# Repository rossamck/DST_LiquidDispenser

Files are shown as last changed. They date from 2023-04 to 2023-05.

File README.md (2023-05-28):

# GUSTAVO - Liquid Dispensing Client

This repo hosts the software and schematics for the GUSTAVO project.

## Installation
### Building from Source

1. Clone this repository:

```bash
git clone https://github.com/rossamck/DST_LiquidDispenser.git
```

2. Navigate to the project directory:
```bash
cd DST_LiquidDispenser
```

3. Install dependencies: 
```bash
npm install
```

4. Run the application:
```bash
npm start
```

### Running release application
1. Download the appropriate installation file for your operating system from the [Releases](https://github.com/rossamck/DST_LiquidDispenser/releases) page.

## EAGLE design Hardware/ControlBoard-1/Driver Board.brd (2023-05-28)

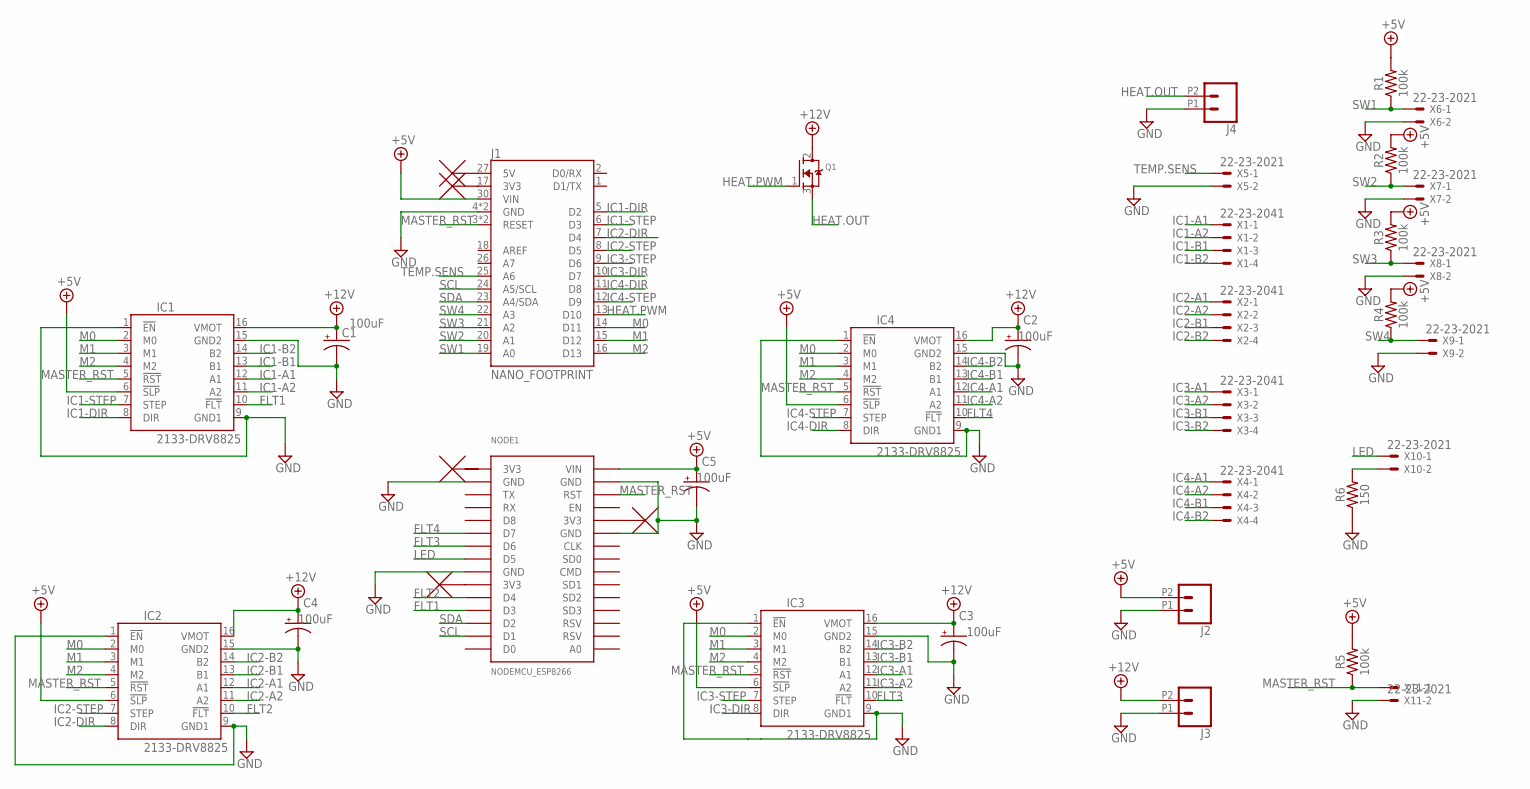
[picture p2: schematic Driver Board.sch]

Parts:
C1, C2, C3, C4, C5: CPOL-USD; PANASONIC_D
IC1, IC2, IC3, IC4: 2133-DRV8825; DRV8825
J1: NANO_FOOTPRINT; NANO
J2, J3, J4: CONN_02SCREWTERMINAL-6.35MM-2; 1X02_6.35_SCREWTERM
NODE1: NODEMCU_ESP8266
Q1: MOSFET-NGDS_TO220V; TO220V
R1, R2, R3, R4, R5: 100k; 0805
R6: 150; 0805
X1, X2, X3, X4: 22-23-2041
X5, X6, X7, X8, X9, X10, X11: 22-23-2021

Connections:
3V3: NODE1.3V3@1 (3V3)
+5V: C5.+, IC1.6 (!SLP), IC2.6 (!SLP), IC3.6 (!SLP), IC4.6 (!SLP), J1.30 (VIN), J2.P2 (1), NODE1.VIN, R1.2, R2.2, R3.2, R4.2, R5.2
+12V: C1.+, C2.+, C3.+, C4.+, IC1.16 (VMOT), IC2.16 (VMOT), IC3.16 (VMOT), IC4.16 (VMOT), J3.P2 (1), Q1.2 (D)
FLT1: IC1.10 (!FLT), NODE1.D3
FLT2: IC2.10 (!FLT), NODE1.D4
FLT3: IC3.10 (!FLT), NODE1.D6
FLT4: IC4.10 (!FLT), NODE1.D7
GND: C1.-, C2.-, C3.-, C4.-, C5.-, IC1.1 (!EN), IC1.9 (GND1), IC1.15 (GND2), IC2.1 (!EN), IC2.9 (GND1), IC2.15 (GND2), IC3.1 (!EN), IC3.9 (GND1), IC3.15 (GND2), IC4.1 (!EN), IC4.9 (GND1), IC4.15 (GND2), J1.4 (GND), J1.29 (GND), J2.P1 (2), J3.P1 (2), J4.P1 (2), NODE1.GND@1 (GND), NODE1.GND@2 (GND), NODE1.GND@3 (GND), NODE1.GND@4 (GND), R6.1, X5.2, X6.2, X7.2, X8.2, X9.2, X11.2
HEAT.OUT: J4.P2 (1), Q1.3 (S)
HEAT.PWM: J1.13 (D10), Q1.1 (G)
IC1-A1: IC1.12 (A1), X1.1
IC1-A2: IC1.11 (A2), X1.2
IC1-B1: IC1.13 (B1), X1.3
IC1-B2: IC1.14 (B2), X1.4
IC1-DIR: IC1.8 (DIR), J1.5 (D2)
IC1-STEP: IC1.7 (STEP), J1.6 (D3)
IC2-A1: IC2.12 (A1), X2.1
IC2-A2: IC2.11 (A2), X2.2
IC2-B1: IC2.13 (B1), X2.3
IC2-B2: IC2.14 (B2), X2.4
IC2-DIR: IC2.8 (DIR), J1.7 (D4)
IC2-STEP: IC2.7 (STEP), J1.8 (D5)
IC3-A1: IC3.12 (A1), X3.1
IC3-A2: IC3.11 (A2), X3.2
IC3-B1: IC3.13 (B1), X3.3
IC3-B2: IC3.14 (B2), X3.4
IC3-DIR: IC3.8 (DIR), J1.10 (D7)
IC3-STEP: IC3.7 (STEP), J1.9 (D6)
IC4-A1: IC4.12 (A1), X4.1
IC4-A2: IC4.11 (A2), X4.2
IC4-B1: IC4.13 (B1), X4.3
IC4-B2: IC4.14 (B2), X4.4
IC4-DIR: IC4.8 (DIR), J1.11 (D8)
IC4-STEP: IC4.7 (STEP), J1.12 (D9)
LED: NODE1.D5, X10.1
M0: IC1.2 (M0), IC2.2 (M0), IC3.2 (M0), IC4.2 (M0), J1.14 (D11)
M1: IC1.3 (M1), IC2.3 (M1), IC3.3 (M1), IC4.3 (M1), J1.15 (D12)
M2: IC1.4 (M2), IC2.4 (M2), IC3.4 (M2), IC4.4 (M2), J1.16 (D13)
MASTER_RST: IC1.5 (!RST), IC2.5 (!RST), IC3.5 (!RST), IC4.5 (!RST), J1.3 (RESET), J1.28 (RESET), NODE1.RST, R5.1, X11.1
unnamed: R6.2, X10.2
SCL: J1.24 (A5/SCL), NODE1.D1
SDA: J1.23 (A4/SDA), NODE1.D2
SW1: J1.19 (A0), R1.1, X6.1
SW2: J1.20 (A1), R2.1, X7.1
SW3: J1.21 (A2), R3.1, X8.1
SW4: J1.22 (A3), R4.1, X9.1
TEMP.SENS: J1.25 (A6), X5.1

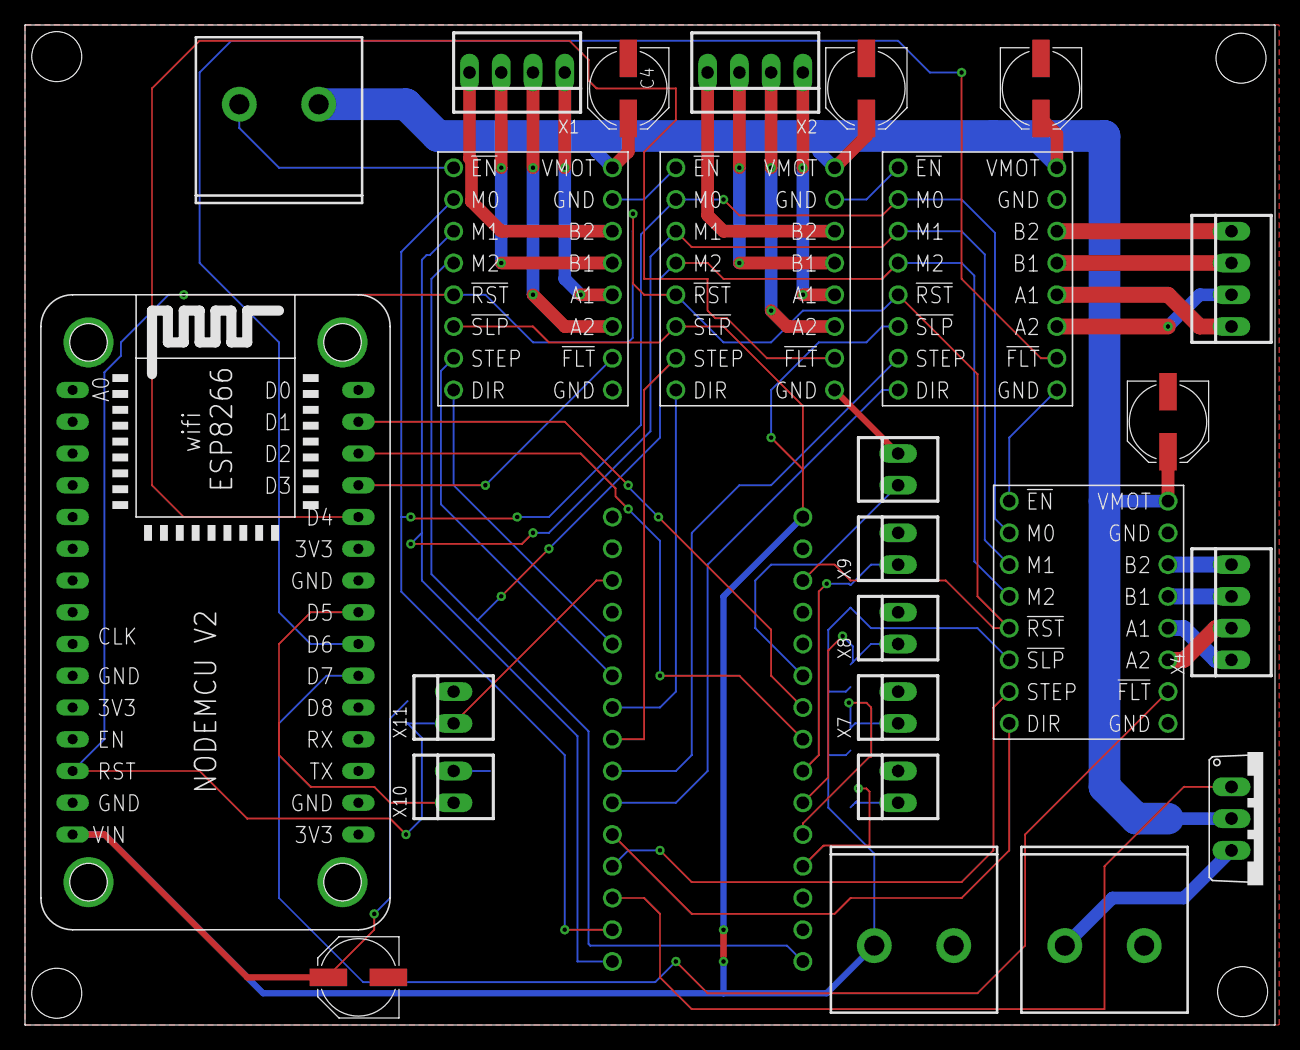
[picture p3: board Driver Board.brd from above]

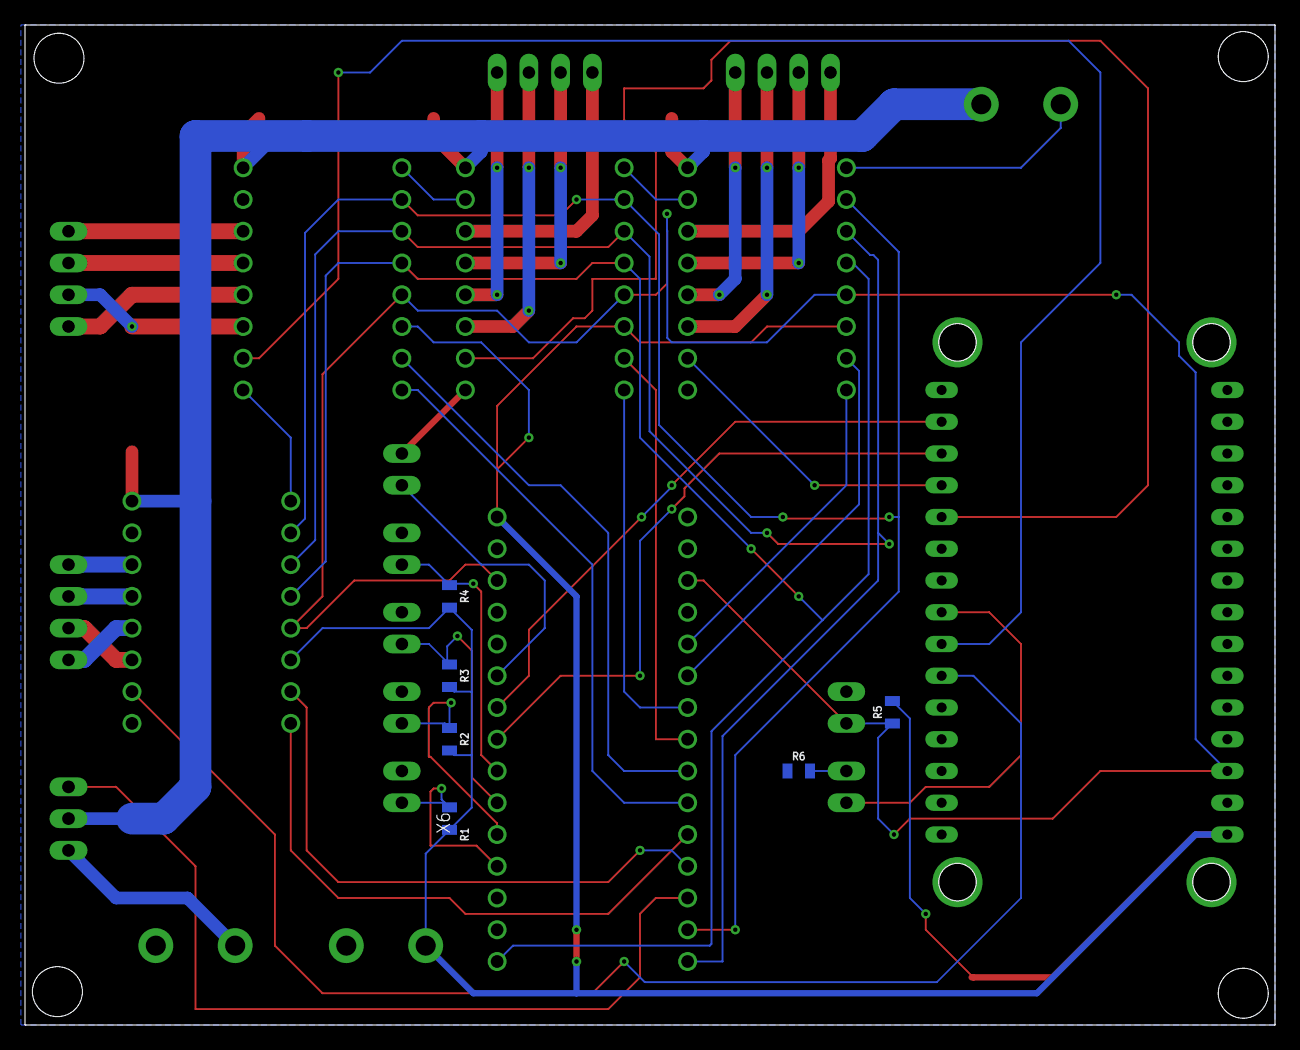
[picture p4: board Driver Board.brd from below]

Board: 2 copper layers, 100.0 x 80.0 mm, 32 parts (6 on the bottom side), 46 nets.

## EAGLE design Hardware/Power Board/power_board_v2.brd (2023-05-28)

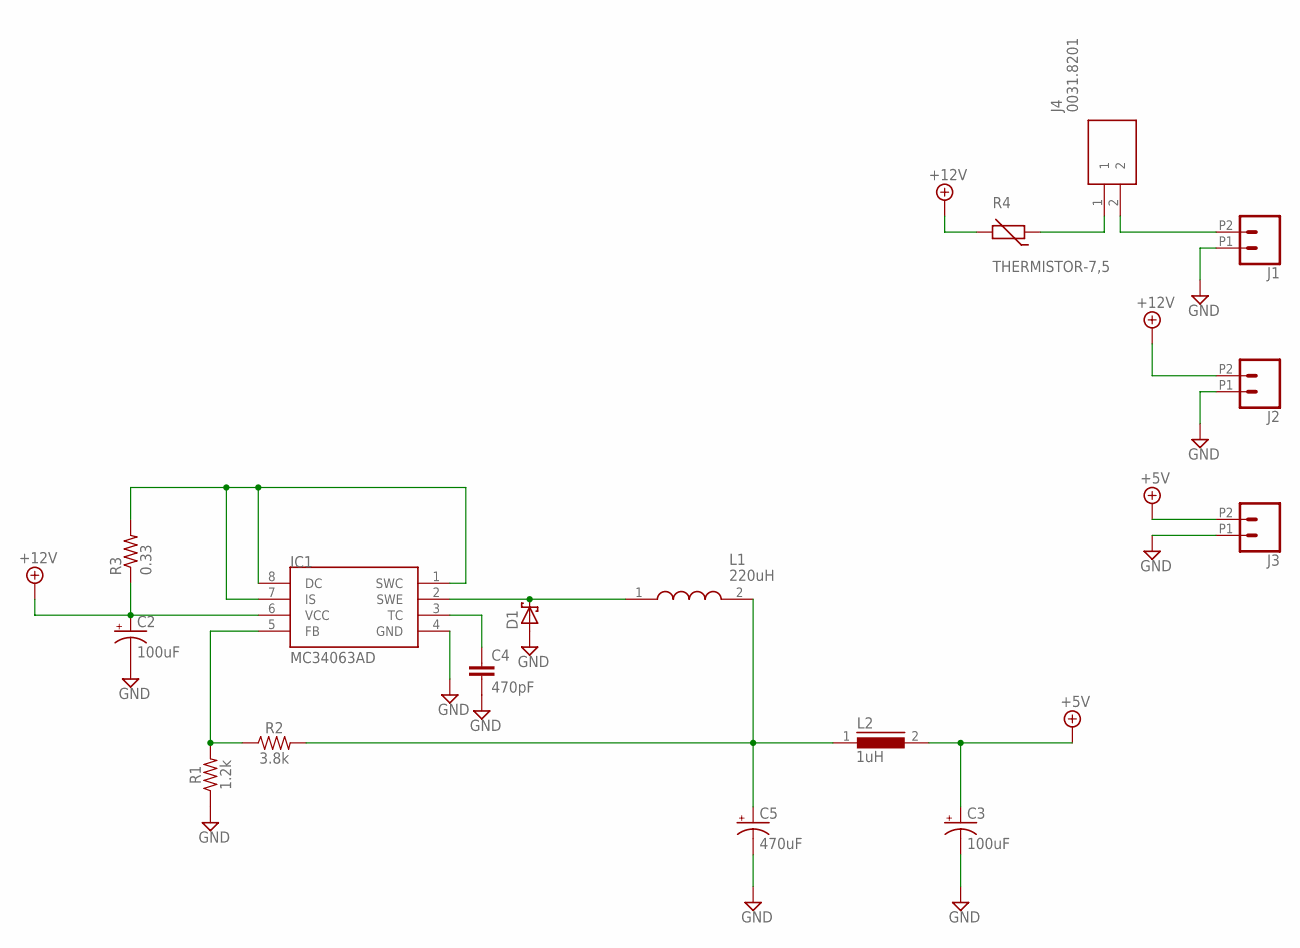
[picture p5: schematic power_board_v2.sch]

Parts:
C2, C3: 100uF; PANASONIC_D
C4: 470pF; C0805
C5: 470uF; PANASONIC_F
D1: SCHOTTKY-DIODEDO41; DO41-10
IC1: MC34063AD; SOIC8
J1, J2, J3: CONN_02SCREWTERMINAL-6.35MM-2; 1X02_6.35_SCREWTERM
J4: 0031.8201
L1: 220uH; WE-TI_809589
L2: 1uH; MICC12
R1: 1.2k; 0805
R2: 3.8k; 0805
R3: 0.33; R2512
R4: THERMISTOR-7,5; R-7,5

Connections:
+5V: C3.+, J3.P2 (1), L2.2
+12V: C2.+, IC1.6 (VCC), J2.P2 (1), R3.1, R4.2
GND: C2.-, C3.-, C4.2, C5.-, D1.A, IC1.4 (GND), J1.P1 (2), J2.P1 (2), J3.P1 (2), R1.1
unnamed: D1.C, IC1.2 (SWE), L1.1
unnamed: C5.+, L1.2, L2.1, R2.2
unnamed: IC1.1 (SWC), IC1.7 (IS), IC1.8 (DC), R3.2
unnamed: C4.1, IC1.3 (TC)
unnamed: IC1.5 (FB), R1.2, R2.1
unnamed: J1.P2 (1), J4.2
unnamed: J4.1, R4.1

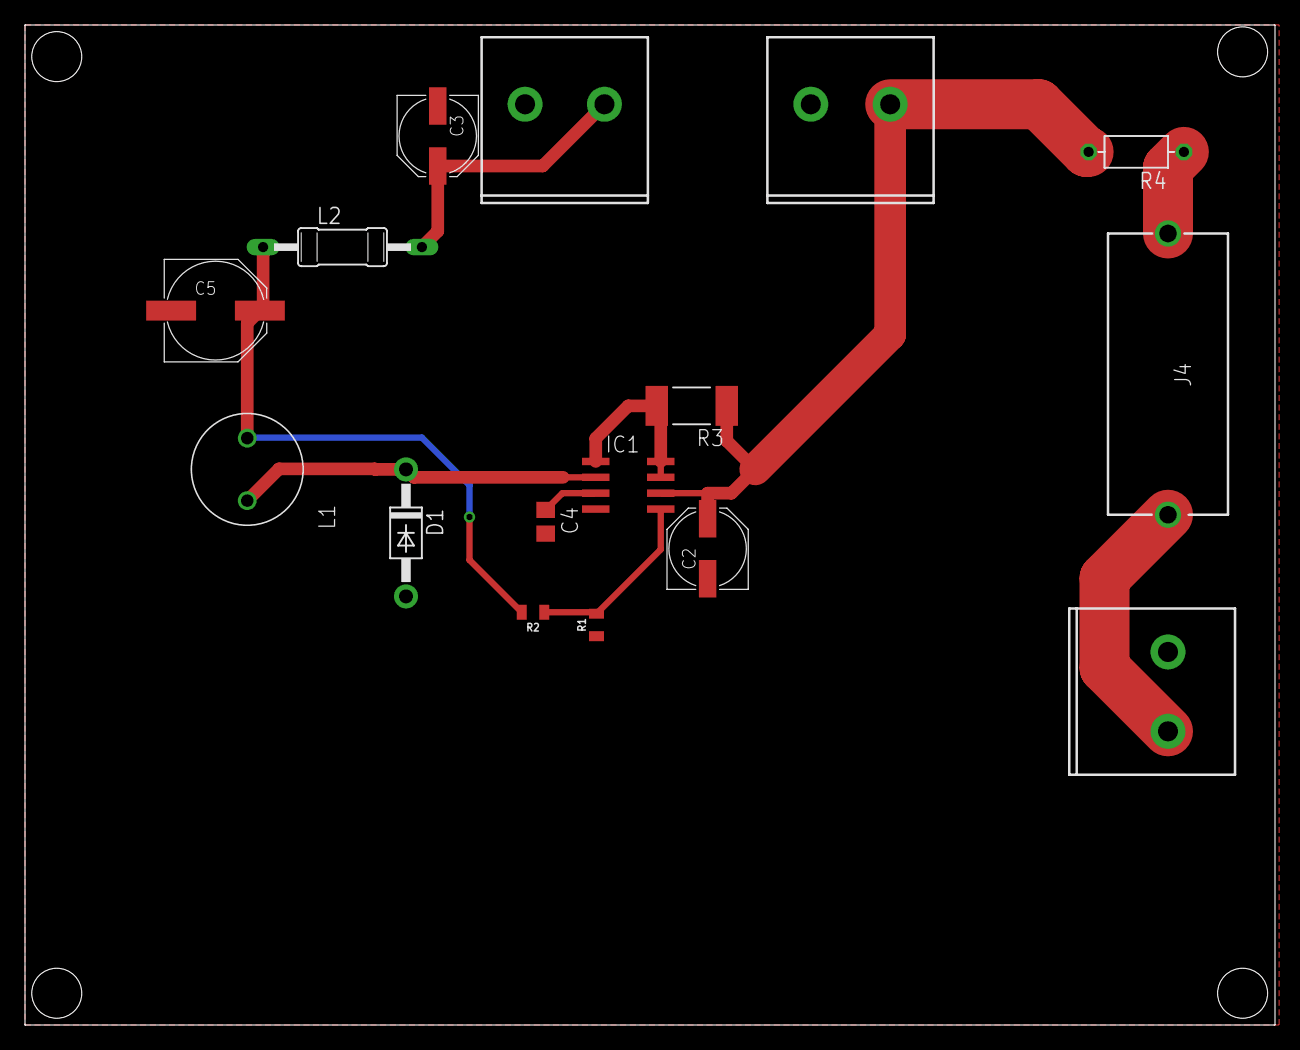
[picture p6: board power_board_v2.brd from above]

Board: 2 copper layers, 100.0 x 80.0 mm, 16 parts (0 on the bottom side), 10 nets.

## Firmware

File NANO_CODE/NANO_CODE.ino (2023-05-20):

#include <Wire.h>
#include <AccelStepper.h>
#include <MultiStepperMotor.h>

// I2C-related definitions
#define SDA_PIN A4
#define SCL_PIN A5

// Stepper motor pin definitions
#define X_DIR_PIN 2
#define X_STEP_PIN 3
#define Y_DIR_PIN 4
#define Y_STEP_PIN 5
#define Z_DIR_PIN 7
#define Z_STEP_PIN 6
#define PIP_DIR_PIN 8
#define PIP_STEP_PIN 9

#define ENABLE 4 // unused

// Microstepping pin definitions
#define M0_PIN 11
#define M1_PIN 12
#define M2_PIN 13

// Limit switch pin definitions
#define LIMIT_1 A0
#define LIMIT_2 A1
#define LIMIT_3 A2
#define LIMIT_4 A3

#define PIP_STEP_AMOUNT 30 // Define the number of steps for the PIP motor

// Stepper motor objects
SingleStepper stepper_X(X_STEP_PIN, X_DIR_PIN, LIMIT_1, true); // Pass true to invert the direction
SingleStepper stepper_Y(Y_STEP_PIN, Y_DIR_PIN, LIMIT_2);
SingleStepper stepper_Z(Z_STEP_PIN, Z_DIR_PIN, LIMIT_3);
SingleStepper stepper_PIP(PIP_STEP_PIN, PIP_DIR_PIN, LIMIT_4, true);
MultiStepper multiStepper(stepper_X, stepper_Y);

struct ReceivedData
{
  bool dataReceived = false;
  bool sendResponse = false;
  bool manualMoveReceived = false;
  String wellId;
  float volume;
  int sourceIndex;

  bool sendCoords = false;
  String axis;
  float value;

  bool moveToLimitReceived = false;
  String moveToLimitAxis;

  bool manualCoordsReceived = false;
  String coordX;
  String coordY;
  String coordZ;

  bool setHomeReceived = false;

  bool zMotorMoveReceived = false;

} receivedData;

float previousX = 0;
float previousY = 0;
float previousZ = 0;
float previousPIP = 0;

int microstep_amount = 8;
int fullturn_400 = 400 * microstep_amount;
int fullturn_200 = 200 * microstep_amount;

void getCurrentPositions(long &xCurrentPosition, long &yCurrentPosition, long &zCurrentPosition, long &pipCurrentPosition)
{
  xCurrentPosition = stepper_X.currentPosition() / microstep_amount;
  yCurrentPosition = stepper_Y.currentPosition() / microstep_amount;
  zCurrentPosition = stepper_Z.currentPosition() / microstep_amount;
  pipCurrentPosition = stepper_PIP.currentPosition() / microstep_amount;
}

void sendPositions(const long xCurrentPosition, const long yCurrentPosition, const long zCurrentPosition, const long pipCurrentPosition)
{
  Wire.write("pos:");
  Wire.write("X=");
  Wire.write(String(xCurrentPosition).c_str());
  Wire.write(",");
  Wire.write("Y=");
  Wire.write(String(yCurrentPosition).c_str());
  Wire.write(",");
  Wire.write("Z=");
  Wire.write(String(zCurrentPosition).c_str());
  Wire.write(",");
  Wire.write("PIP=");
  Wire.write(String(pipCurrentPosition).c_str());
  Wire.write('\0'); // Add a null character to indicate the end of the message
}

void sendCurrentPositions()
{
  long xCurrentPosition, yCurrentPosition, zCurrentPosition, pipCurrentPosition;
  getCurrentPositions(xCurrentPosition, yCurrentPosition, zCurrentPosition, pipCurrentPosition);
  sendPositions(xCurrentPosition, yCurrentPosition, zCurrentPosition, pipCurrentPosition);
}

void moveMotors(float currentX, float currentY)
{
  float deltaX = currentX - previousX;
  float deltaY = currentY - previousY;

  long stepsX = deltaX * microstep_amount;
  long stepsY = deltaY * microstep_amount;

  Serial.print("deltaX=");
  Serial.print(deltaX);
  Serial.print(", deltaY=");
  Serial.print(deltaY);

  multiStepper.move(stepsX, stepsY);
  multiStepper.runToPosition();

  previousX = currentX;
  previousY = currentY;
}

void moveZMotor(float currentZ)
{
  float deltaZ = currentZ - previousZ;
  long stepsZ = deltaZ * microstep_amount;

  Serial.print("deltaZ=");
  Serial.print(deltaZ);

  stepper_Z.move(stepsZ);
  stepper_Z.runToPosition();

  previousZ = currentZ;
}

void movePIPMotor()
{
  long stepsPIP = PIP_STEP_AMOUNT * microstep_amount;

  Serial.print("Moving PIP Motor by ");
  Serial.print(stepsPIP);
  Serial.println(" steps");

  stepper_PIP.move(stepsPIP);
  stepper_PIP.runToPosition();

  previousPIP += PIP_STEP_AMOUNT; // Update previousPIP to reflect the new position
}

void setup()
{
  // I2C setup
  Wire.begin(8);
  Wire.onReceive(receiveEvent);
  Wire.onRequest(requestEvent);
  Serial.begin(9600);
  Serial.println("Starting Nano");

  //   pinMode(SDA_PIN, INPUT_PULLUP);
  // pinMode(SCL_PIN, INPUT_PULLUP);

  // Stepper motor setup
  pinMode(M0_PIN, OUTPUT);
  pinMode(M1_PIN, OUTPUT);
  pinMode(M2_PIN, OUTPUT);
  pinMode(ENABLE, OUTPUT);
  digitalWrite(M0_PIN, HIGH);
  digitalWrite(M1_PIN, HIGH);
  digitalWrite(M2_PIN, LOW);
  multiStepper.setMaxSpeed(10000, 10000);
  multiStepper.setAcceleration(2000, 2000);
  stepper_Z.setMaxSpeed(10000);
  stepper_Z.setAcceleration(2000);
  stepper_PIP.setMaxSpeed(10000);
  stepper_PIP.setAcceleration(2000);

  // Limit switch setup
  pinMode(LIMIT_1, INPUT_PULLUP);
  pinMode(LIMIT_2, INPUT_PULLUP);
  pinMode(LIMIT_3, INPUT_PULLUP);
  pinMode(LIMIT_4, INPUT_PULLUP);

  Serial.println("Calibrating Z...");
  // stepper_Z.runToLimit();

  //       stepper_Z.move(500 * microstep_amount);  // Move by deltaY number of microsteps
  //     stepper_Z.runToPosition();
}

void loop()
{
  if (receivedData.dataReceived)
  {
    Serial.print("Received well ID: ");
    Serial.println(receivedData.wellId);
    Serial.print("Received volume: ");
    Serial.println(receivedData.volume);
    Serial.print("Received source index: ");
    Serial.println(receivedData.sourceIndex);
    Serial.print("Received x: ");
    Serial.println(receivedData.coordX);
    Serial.print("Received y: ");
    Serial.println(receivedData.coordY);

    float currentX = receivedData.coordX.toFloat();
    float currentY = receivedData.coordY.toFloat();
    float currentZ = receivedData.coordZ.toFloat();

    moveMotors(currentX, currentY);
    // Move Z motor down

    moveZMotor(50);

    movePIPMotor();

    // Move Z motor back up
    moveZMotor(100);

    Serial.print("Send well response for: ");
    Serial.println(receivedData.wellId);

    receivedData.sendResponse = true;
    receivedData.dataReceived = false;
  }
  else if (receivedData.zMotorMoveReceived)
  {
    float currentZ = receivedData.coordZ.toFloat();
    moveZMotor(currentZ);
    receivedData.zMotorMoveReceived = false;
  }

  else if (receivedData.manualMoveReceived)
  {
    Serial.print("Received Data: ");
    Serial.print("Axis = ");
    Serial.print(receivedData.axis);
    Serial.print(", Value = ");
    Serial.println(receivedData.value);

    if (receivedData.axis == "X")
    {
      float deltaX = receivedData.value - previousX;
      stepper_X.move(deltaX * microstep_amount); // Move by deltaX number of microsteps
      stepper_X.runToPosition();
      previousX = receivedData.value;
    }
    else if (receivedData.axis == "Y")
    {
      float deltaY = receivedData.value - previousY;
      stepper_Y.move(deltaY * microstep_amount); // Move by deltaY number of microsteps
      stepper_Y.runToPosition();
      previousY = receivedData.value;
    }
    else if (receivedData.axis == "Z")
    {
      float deltaZ = receivedData.value - previousZ;
      Serial.print("DeltaZ = ");
      Serial.println(deltaZ);
      stepper_Z.move(deltaZ * microstep_amount); // Move by deltaZ number of microsteps
      stepper_Z.runToPosition();
      previousZ = receivedData.value;
    }
    else if (receivedData.axis == "PIP")
    {
      float deltaPIP = receivedData.value - previousPIP;
      stepper_PIP.move(deltaPIP * microstep_amount); // Move by deltaPIP number of microsteps
      stepper_PIP.runToPosition();
      previousPIP = receivedData.value;
    }
    // Check current motor positions:
    long xCurrentPosition = stepper_X.currentPosition();
    long yCurrentPosition = stepper_Y.currentPosition();
    long zCurrentPosition = stepper_Z.currentPosition();
    long pipCurrentPosition = stepper_PIP.currentPosition();
    Serial.print("X current position: ");
    Serial.println(xCurrentPosition);
    Serial.print("Y current position: ");
    Serial.println(yCurrentPosition);
    Serial.print("Z current position: ");
    Serial.println(zCurrentPosition);
    Serial.print("PIP current position: ");
    Serial.println(pipCurrentPosition);
    sendCurrentPositions();
    receivedData.sendCoords = true;
    receivedData.manualMoveReceived = false;
  }

  else if (receivedData.moveToLimitReceived)
  {
    if (receivedData.moveToLimitAxis == "X")
    {
      stepper_X.runToLimit();
    }
    else if (receivedData.moveToLimitAxis == "Y")
    {
      stepper_Y.runToLimit();
    }
    else if (receivedData.moveToLimitAxis == "Z")
    {
      stepper_Z.runToLimit();
    }
    receivedData.sendCoords = true;

    receivedData.moveToLimitReceived = false;
  }

  else if (receivedData.manualCoordsReceived)
  {
    float currentX = receivedData.coordX.toFloat();
    float currentY = receivedData.coordY.toFloat();
    float currentZ = receivedData.coordZ.toFloat();

    moveMotors(currentX, currentY); // And also here

    receivedData.sendCoords = true;
    receivedData.manualCoordsReceived = false;
  }

  else if (receivedData.setHomeReceived)
  {
    Serial.println("Setting home position!");
    stepper_X.setCurrentPosition(0);
    stepper_Y.setCurrentPosition(0);
    stepper_Z.setCurrentPosition(0);
    stepper_PIP.setCurrentPosition(0);

    receivedData.setHomeReceived = false;
  }

  delay(100);
}
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

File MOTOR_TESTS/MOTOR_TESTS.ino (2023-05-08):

#include <AccelStepper.h>
#include <MultiStepperMotor.h>


// Define the stepper motor connections
// IC1 pin definitions
#define X_DIR_PIN 2
#define X_STEP_PIN 3


// IC2 pin definitions
#define Y_DIR_PIN 4
#define Y_STEP_PIN 5

// IC3 pin definitions
#define Z_DIR_PIN 7
#define Z_STEP_PIN 6

// IC4 pin definitions
#define PIP_DIR_PIN 8
#define PIP_STEP_PIN 9


#define ENABLE 4 //unused

// Define the microstepping pins
#define M0_PIN 11
#define M1_PIN 12
#define M2_PIN 13


//Full turn equal to number of steps per full rotation * microstepping amount
//Currently using 1/8 microstepping
int microstep_amount = 8;
int fullturn_400 = 400 * microstep_amount;
int fullturn_200 = 200 * microstep_amount;

// Initialize stepper motor and multi-stepper objects
MultiStepperMotor stepper_X(X_STEP_PIN, X_DIR_PIN);
MultiStepperMotor stepper_Y(Y_STEP_PIN, Y_DIR_PIN);
MultiStepperMotor stepper_Z(Z_STEP_PIN, Z_DIR_PIN);
MultiStepperMotor stepper_PIP(PIP_STEP_PIN, PIP_DIR_PIN);
MultiStepperXY multiStepper(stepper_X, stepper_Y);

void setup() {
  // Define the microstepping pins as outputs
  pinMode(M0_PIN, OUTPUT);
  pinMode(M1_PIN, OUTPUT);
  pinMode(M2_PIN, OUTPUT);
  pinMode(ENABLE, OUTPUT);

  // Set the microstepping mode to 1/8 step
  digitalWrite(M0_PIN, HIGH);
  digitalWrite(M1_PIN, HIGH);
  digitalWrite(M2_PIN, LOW);

  // Set the maximum speed and acceleration
  multiStepper.setMaxSpeed(10000);
  multiStepper.setAcceleration(2000);

  Serial.begin(115200); //Enable serial comms for debugging
}

void loop() {
  // Move the X direction motor forward 10 rotations (say halfway on the X axis for argument sake)

    Serial.println("Moving X and Y simultaneously");
  multiStepper.move(fullturn_400 * 10, fullturn_400 * 10);
  multiStepper.runToPosition();
  
  Serial.println("Rotating X clockwise 10 times");
  stepper_X.move(fullturn_400*10);
  stepper_X.runToPosition();

  // Move in Y direction
  Serial.println("Rotating Y clockwise 10 times");
  stepper_Y.move(fullturn_400*10);
  stepper_Y.runToPosition();

  //Lower pippete with Z axis motor (3 full rotations)
  Serial.println("Rotating Z clockwise 3 times");
  stepper_Z.move(fullturn_200*3);
  stepper_Z.runToPosition();

  //Dispense pipette (half rotation forward then back 3 times - needs editing)
  for (int i = 0; i < 3; i++) {
    Serial.println("Clicking pipette");
    stepper_PIP.move(fullturn_200*0.5);
    stepper_PIP.runToPosition();
    stepper_PIP.move(-fullturn_200*0.5);
    stepper_PIP.runToPosition();
  }
  

  //Move pippete back up with Z axis motor (3 full rotations)
  Serial.println("Rotating Z anticlockwise 3 times");
  stepper_Z.move(-fullturn_200*3);
  stepper_Z.runToPosition();

  // Move the Y direction motor back 10 rotations
  Serial.println("Rotating Y anticlockwise 10 times");
  stepper_Y.move(-fullturn_400*10);
  stepper_Y.runToPosition();

  // Move the X direction motor back 10 rotations
  Serial.println("Rotating X anticlockwise 10 times");
  stepper_X.move(-fullturn_400*10);
  stepper_X.runToPosition();
}

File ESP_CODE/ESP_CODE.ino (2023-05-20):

#include <ESP8266WiFi.h>
#include <WiFiClient.h>
#include <ESP8266WebServer.h>
#include <WebSocketsServer.h>
#include <vector>
#include <Wire.h>
#include <Ticker.h>
#include <ArduinoJson.h>
#define SDA_PIN 4 // D2 on ESP8266
#define SCL_PIN 5 // D1 on ESP8266

#define ARDUINO_NANO_I2C_ADDR 8

const char *ssid = "VM6701124_2G";
const char *password = "fnDdpj9q6qdt";
// const char* ssid = "iPhone (3)";
// const char* password = "13245768";
const int ledPin = LED_BUILTIN;

ESP8266WebServer server(80);
WebSocketsServer webSocket(81);

bool ledState = false;
bool dispensing = false;

struct Well
{
  String wellId;
  float volume;
  int sourceIndex;
  int x;
  int y;
};

StaticJsonDocument<200> doc;

std::vector<Well> selectedWells;
std::vector<Well>::iterator currentWell;
int currentJobId = -1; // Initialize to -1 or another value that indicates no jobId has been set

void sendJobIdMessage(int jobId)
{
  String jobIdMessage = "jobId:" + String(jobId);
  webSocket.broadcastTXT(jobIdMessage);
}

String requestDataFromNano()
{
  while (true)
  {
    Wire.requestFrom(ARDUINO_NANO_I2C_ADDR, 32);
    String response = "";
    while (Wire.available())
    {
      char c = Wire.read();
      if (c == '\0')
        break;
      response += c;
    }

    if (response.startsWith("finished"))
    {
      Serial.print("Received finished message:");
      Serial.println(response);
      return response;
    }

    else if (response.startsWith("pos:"))
    {
      Serial.print("Received position message:");
      Serial.println(response);
      return response;
    }

    if (response != "")
    {
      break; // Break out of the loop if a non-empty message is received
    }

    delay(100); // Wait for 100ms before checking again
  }
  return "";
}

void connectToWiFi()
{
  Serial.println("Connecting to WiFi...");
  WiFi.mode(WIFI_STA);
  WiFi.begin(ssid, password);

  while (WiFi.status() != WL_CONNECTED)
  {
    delay(500);
    Serial.print(".");
  }

  Serial.println("");
  Serial.println("WiFi connected");
  Serial.println("IP address: ");
  Serial.println(WiFi.localIP());
}

void createAccessPoint()
{
  Serial.println("Creating access point...");
  WiFi.mode(WIFI_AP);
  IPAddress localIP(192, 168, 4, 1);
  IPAddress gateway(192, 168, 4, 1);
  IPAddress subnet(255, 255, 255, 0);
  WiFi.softAPConfig(localIP, gateway, subnet);
  WiFi.softAP("ESP8266AP", "password");

  Serial.println("");
  Serial.println("Access Point created");
  Serial.println("IP address: ");
  Serial.println(WiFi.softAPIP());
}

// proto
void handleDispensing();
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

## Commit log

2023-03-26 added motor testing code
2023-04-12 added ability to track currently dispensing well
2023-05-08 updated arduino test files
2023-05-08 updated motor control code
2023-05-09 updated arduino code
2023-05-15 coordinate calibration
2023-05-28 updated readme and added hardware
    [Driver Board v2.brd, Driver Board v2.sch, Driver Board.brd, Driver Board.sch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]

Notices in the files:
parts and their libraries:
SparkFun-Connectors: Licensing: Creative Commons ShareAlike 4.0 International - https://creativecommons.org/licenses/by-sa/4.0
